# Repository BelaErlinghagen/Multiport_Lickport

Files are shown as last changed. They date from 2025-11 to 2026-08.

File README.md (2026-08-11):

# The Multiport Setup

**A behavioral setup for mice with 16 reward ports, multiple light/sound cues and real time pose estimation.**

<p align="center">
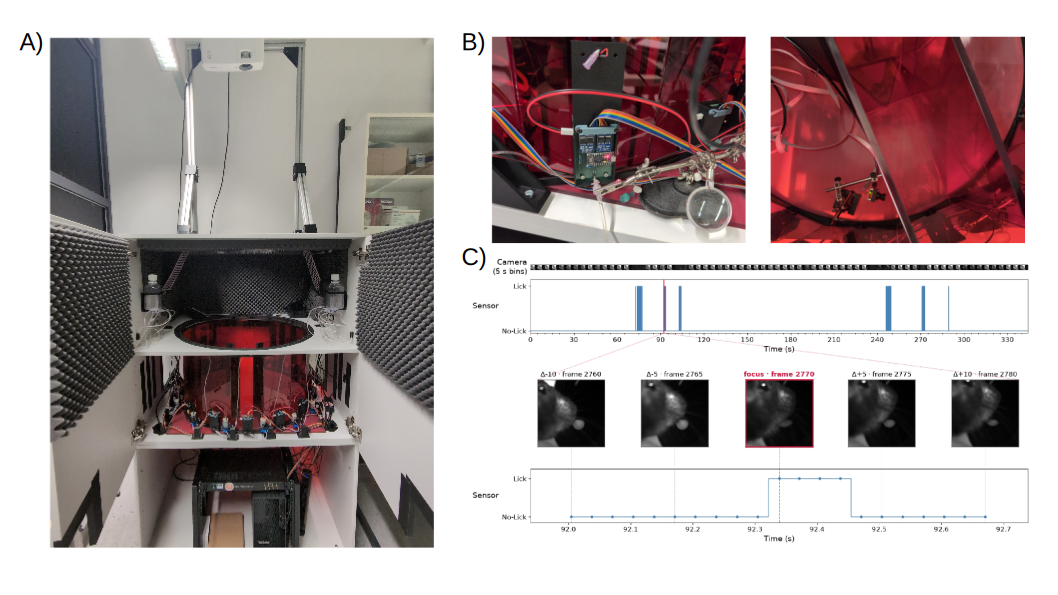
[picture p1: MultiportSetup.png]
Overview of the Multiport Setup
  
</p>

<p align="center">
  <em>
    <b>Figure 1: The Multiport Setup.</b>
    <b>A)</b> Complete view of the Multiport Setup.
    <b>B)</b> Testing adjustments to the setup to show that the capacitive sensor of the Lick-O-Tron detects mouse licks.
    A Basler daA1440 was used to record the lickport. The mouse was given condensed milk (white droplet in C) manually through the shown tube.
    <b>C)</b> <i>Top:</i> Timeline over the entire session, with sensor activations marked as blue bars.
    <i>Bottom:</i> Zoom into one lick detection.
  </em>
</p>

---

## Table of Contents

- [Components of the Multiport Setup](#components-of-the-multiport-setup)
  - [Arena](#arena)
  - [Lick-O-Tron and PORTMASTER](#lick-o-tron-and-portmaster)
  - [Computer](#computer)
  - [Projector](#projector)
  - [Camera](#camera)
  - [Screens](#screens)
- [The Lick-O-Tron Lickport](#the-lick-o-tron-lickport)
  - [Design](#design)
  - [Assembly](#assembly)
    - [Parts](#parts)
    - [Step 1: Soldering](#step-1-soldering)
    - [Step 2: Uploading the code and testing the sensor](#step-2-uploading-the-code-and-testing-the-sensor)
    - [Step 3: Preparing the cannula](#step-3-preparing-the-cannula)
    - [Step 4: Assembly](#step-4-assembly)
    - [Step 5: Add the pump](#step-5-add-the-pump)
  - [Usage](#usage)
- [The PORTMASTER](#the-portmaster)
  - [Design](#design-1)
  - [Assembly](#assembly-1)
    - [Parts](#parts-1)
    - [Step 1: Solder pins and connector pieces to the PCB](#step-1-solder-pins-and-connector-pieces-to-the-pcb)
    - [Step 2: Wiring](#step-2-wiring)
  - [Usage](#usage-1)
- [Credit](#credit)

---

## Components of the Multiport Setup

### Arena

The arena is built from 16 [red acrylic wall panels](ArenaFiles/ArenaWall.stp), held together by 16 [connector pieces](ArenaFiles/AnglePiece.stp). This circular assembly stands on a sheet of acrylic that has been roughened on one side, which makes it more comfortable for the mice to walk on and prevents light projected onto the arena floor from being reflected.

In addition to the circular Multiport arena, two inlets were created to form a Y-Maze.

### Lick-O-Tron and PORTMASTER

The **Lick-O-Tron** is a self-built lickport module consisting of a capacitive sensor, an LED and a MOSFET relay to trigger a pump or valve.

The **PORTMASTER** is a hub that connects all Lick-O-Trons to the master Arduinos and delivers power to the pumps.

Both components are documented in detail below: see [The Lick-O-Tron Lickport](#the-lick-o-tron-lickport) and [The PORTMASTER](#the-portmaster).

### Computer

The computer used in this build was a Lenovo Thinkstation with the following specifications:

| Component | Specification |
| :--- | :--- |
| CPU | Intel(R) Core(TM) i7-14700K |
| GPU | Nvidia GeForce RTX 4060 |
| OS  | Ubuntu 24.04 |

To run live inference with DeepLabCut, CUDA was installed alongside the necessary Nvidia GPU drivers. Pixi was used to manage the Python environment of the software; the `.lock` and `.toml` files can be found in this repository.

### Projector

A BenQ Cinema Master Projector was mounted approximately 200 cm above the arena floor.

### Camera

A Basler daA3840-45uc camera with an Evetar lens (E3417A F2.4 f2.5mm 1/1.8") was mounted 40 cm below the arena floor.

### Screens

In the Y-Maze configuration, two Adafruit screens (5" 800x480 HDMI Backpack) were used to display patterns for the mice. The screens were mounted on [custom holders](ArenaFiles/YMaze_ScreenHolder.stp) that fit the Y-Maze configuration, and were connected directly to the computer via HDMI.

---

# Documentation for the Lick-O-Tron and the PORTMASTER

The Lick-O-Tron lickport and the PORTMASTER connectivity board are the two major components that act together in the automated Multiport system. Their design, assembly and usage are explained in detail below. The files needed to recreate the two modules can be found in their respective folders.

## The Lick-O-Tron Lickport

The idea behind the Lick-O-Tron was to create a lickport for behavioral mouse experiments that can:

1. Register lick events via a capacitive sensor.
2. Connect to up to two peristaltic pumps, which can independently eject precise volumes of liquid.
3. Allow flexible control of an LED located next to the needle.

### Design

The Lick-O-Tron contains three submodules: one Arduino proMicro and two MOSFET relay modules. The Arduino proMicro, as well as the power outlets of the MOSFET relay modules, receive power via the main connector (8-pin plug).

The Arduino's job is to register licks via a capacitive sensor — a cannula connected to the single pin at the bottom of the Lick-O-Tron. This is achieved with the code found [here](Lick-O-Tron/LickportArduinoCode.ino). The Arduino then transmits binary data about lick events to the Arduino Megas housed on the PORTMASTER.

The MOSFET modules are activated by the master Arduinos on the PORTMASTER and can trigger peristaltic pumps (or valves, etc.). The idea is that lick information is received by the master Arduinos, which then activate the pumps at set timepoints and with set PWM, depending on the needs of the experimenter. This allows for very flexible control of liquid dispensation. The Lick-O-Tron further connects the master Arduinos to an LED, which can be controlled independently.

<p align="center">
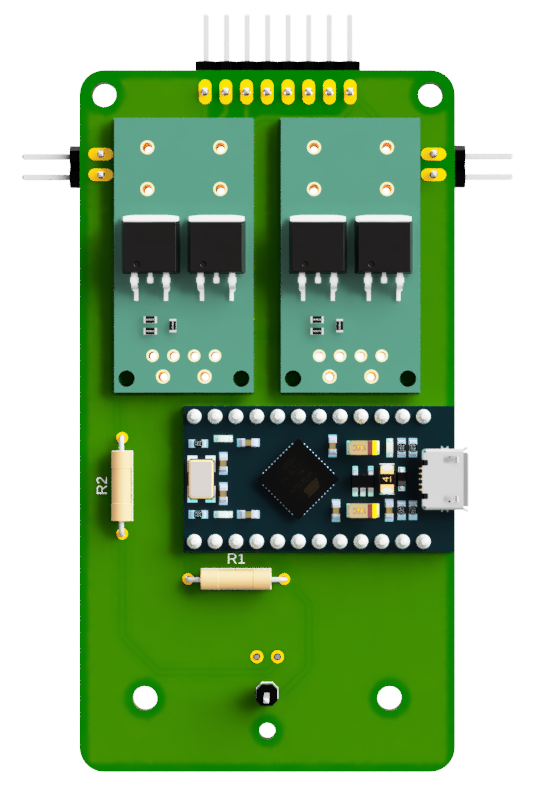
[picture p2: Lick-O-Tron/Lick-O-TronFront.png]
Lick-O-Tron front
  
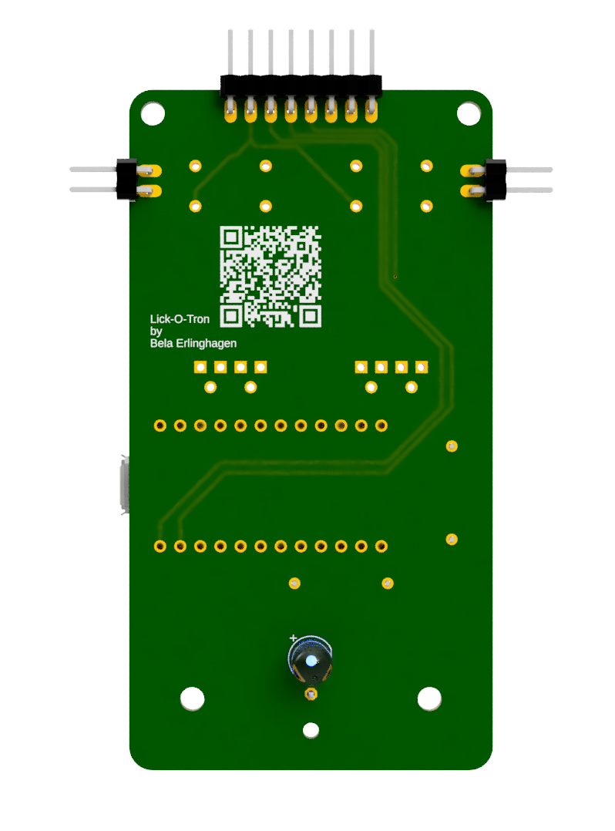
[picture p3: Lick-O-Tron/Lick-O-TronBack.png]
Lick-O-Tron back
  
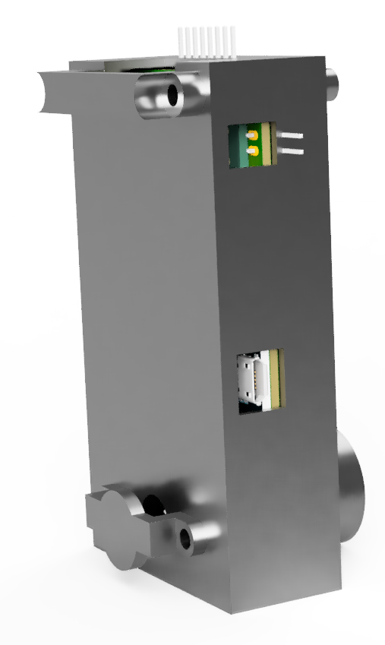
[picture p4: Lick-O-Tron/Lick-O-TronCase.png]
Lick-O-Tron case
  
</p>

<p align="center">
  <em><b>Figure 2:</b> 3D CAD model renderings for the Lick-O-Tron (left: front, middle: back, right: case). Note that the Pin Connectors are not depicted correctly in this Figure: The 8 Pin Header is straight and supposed to be soldered onto the other side of the PCB and the two angular 2 Pin Headers are also depicted on the wrong side of the PCB.</em>
</p>

### Assembly

#### Parts

| Item | Quantity | Manufactured by | EAN |
| :--- | ---: | :--- | ---: |
| Joy It proMicro | 1 | Joy It | 4250236822907 |
| MOSFET Relay Module | 2 | for example GERUI | 0744243396666 |
| Mini Peristaltic Pump | 1 (up to 2) | Whadda | 5410329730017 |
| Lick-O-Tron PCB | 1 | Eurocircuits | None: see folder in repo |
| Lick-O-Tron Case Parts | 1 each | 3D printed | None: see folder in repo |
| LED (white) | 1 | TRU Components | 2050004902785 |
| 10 MOhm Resistor (R1) | 1 | TRU Components | 2050004926057 |
| 470 Ohm Resistor (R2) | 1 | TRU Components | 4016139313023 |
| M3 Screws | 4 | Toolcraft | 4064161107578 |
| M3 Nuts | 4 | SWG Hox | 4053056028951 |
| Sterican Cannula | 2 | Roth | - |

#### Step 1: Soldering

With the PCB, the proMicro, the LED, the resistors, some pins and the relay modules at hand, the first step is to solder all of these components onto the PCB. By the end, the PCB should look similar to what is shown in Figure 2.

#### Step 2: Uploading the code and testing the sensor

Upload the Lick-O-Tron [code](Lick-O-Tron/LickportArduinoCode.ino) from this repository to the Joy It proMicro using the Arduino IDE. Then use the serial monitor to test whether touching the sensor pin registers something.

#### Step 3: Preparing the cannula

<p align="center">
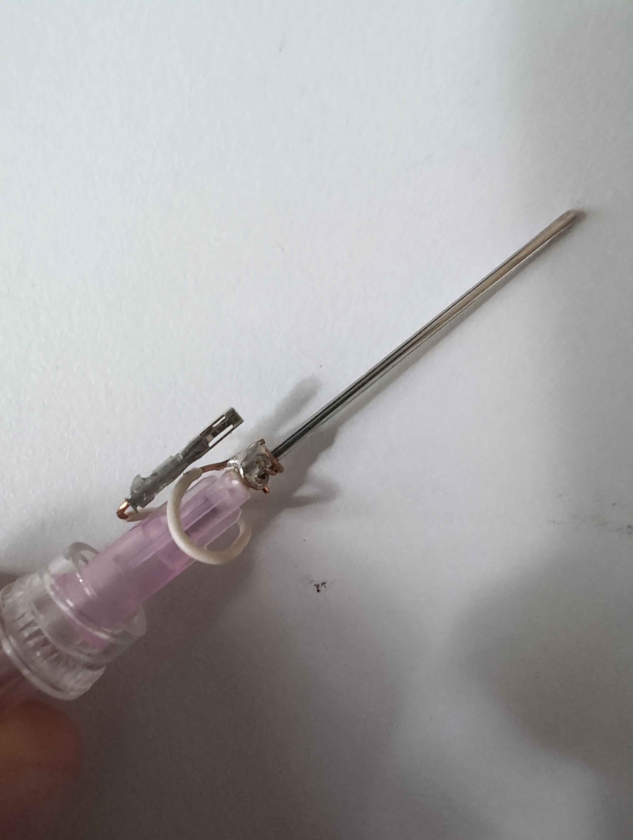
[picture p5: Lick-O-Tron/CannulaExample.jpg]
Example cannula assembly
  
</p>

<p align="center">
  <em><b>Figure 3:</b> Example cannula assembly.</em>
</p>

To electrically connect the cannula to the sensor pin, a wire was wrapped around the cannula and clamped to it, and a second wire was then soldered onto the first one. This second wire was soldered to a pin connector piece, which connects to the sensor pin.

#### Step 4: Assembly

Once all these pieces are ready, the Lick-O-Tron can be assembled. In the Multiport build previewed here, the PCB was simply placed into the 3D-printed chamber and everything was screwed together directly onto the arena, where the spout frame had already been fixed into the acrylic sheets.

#### Step 5: Add the pump

To add the pump, solder two wires to the solder flags and their other ends to a pin connector. To rebuild the setup shown here exactly, 3D print the pump holder pieces and attach the pump as shown in Figure 4.

### Usage

<p align="center">
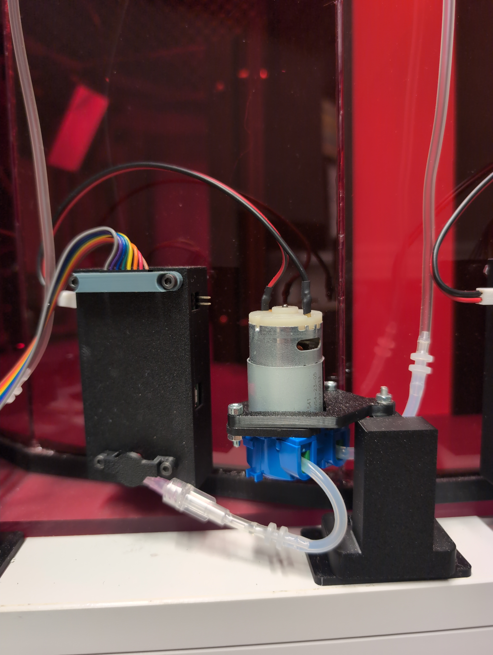
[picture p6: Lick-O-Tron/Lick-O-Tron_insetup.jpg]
Assembled Lick-O-Tron in the setup
  
</p>

<p align="center">
  <em><b>Figure 4:</b> All pieces together.</em>
</p>

The Lick-O-Tron is connected to the PORTMASTER via an 8-band ribbon cable. One PORTMASTER can control up to 16 Lick-O-Trons.

---

## The PORTMASTER

<p align="center">
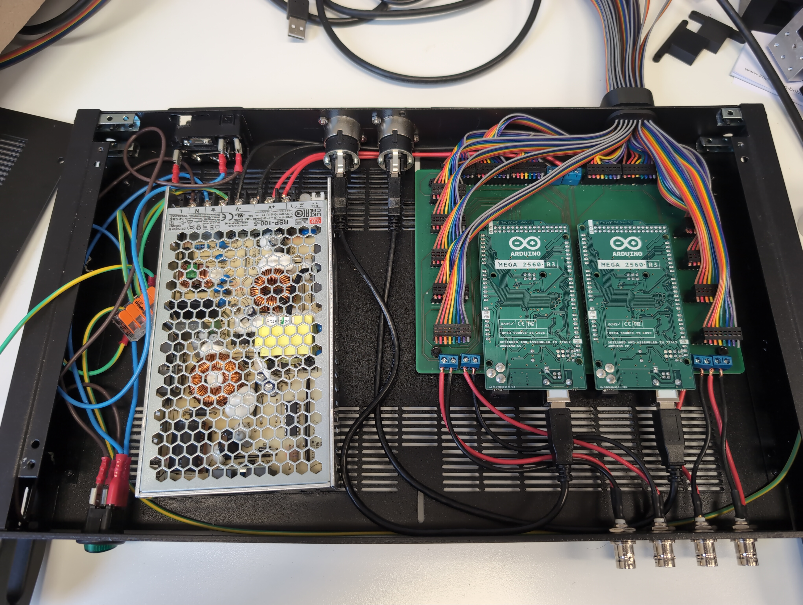
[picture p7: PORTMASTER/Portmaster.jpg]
The PORTMASTER rack with the lid opened
  
</p>

<p align="center">
  <em><b>Figure 5:</b> The PORTMASTER rack, lid opened.</em>
</p>

### Design

The PORTMASTER is designed to:

- power up to five 6 V pumps comfortably (more are possible);
- provide an easily accessible interface between the Arduinos and the computer, BNCs and power supply.

### Assembly

#### Parts

| Item | Quantity | Manufactured by | EAN |
| :--- | ---: | :--- | ---: |
| Arduino Mega 2560 Rev3 | 2 | Arduino | 7630049200067 |
| 8-band ribbon cable | - | - | - |
| 8-Way IDC Connector Female for Cable, 1 Row | 32 | Wurth Elektronik | 661008151923 (Mf. part #) |
| PORTMASTER PCB | 1 | Eurocircuits | None: see folder in repo |
| RSP-100-5 SMPSU 5V DC 20A 100W | 1 | MEAN WELL | 4711287435657 |

> **Note:** The remaining parts visible in Figure 5 have been left out on purpose, as they are specific to the space in which the Multiport Setup — and especially the PORTMASTER — was housed.

#### Step 1: Solder pins and connector pieces to the PCB

To connect the two Arduino Megas to the PCB, first solder the pins and the connector pieces for the power supply and the BNCs onto the PCB.

#### Step 2: Wiring

Once the Arduinos are in place, all that is left to do is the wiring. The 16 Lick-O-Trons are connected using an 8-band ribbon cable together with two 8-way IDC connectors, one going on the Lick-O-Tron and one on the PORTMASTER. Then the power supply needs to be connected to mains power and to the PCB. In the build showcased here, male BNC plugs were also connected to the PCB.

> **Safety:** Make sure to properly ground the casing of the PORTMASTER.

### Usage

The PORTMASTER can be connected to a computer via two USB-B to USB-A cables. It can then be used with the [custom software](Multiport_Code) in this repository.

---

## Credit

The Lick-O-Tron and the PORTMASTER were conceptualized and designed by Bela Erlinghagen, with extensive support from [Trace Robbins](https://github.com/R-Trace) and [Ben Escribano](https://github.com/BenjaminEscribano) of the iBehave CADRE ([website](https://ibehave.nrw/ibots-platform/cadre/), [GitHub](https://github.com/iBehave-CADRE)).

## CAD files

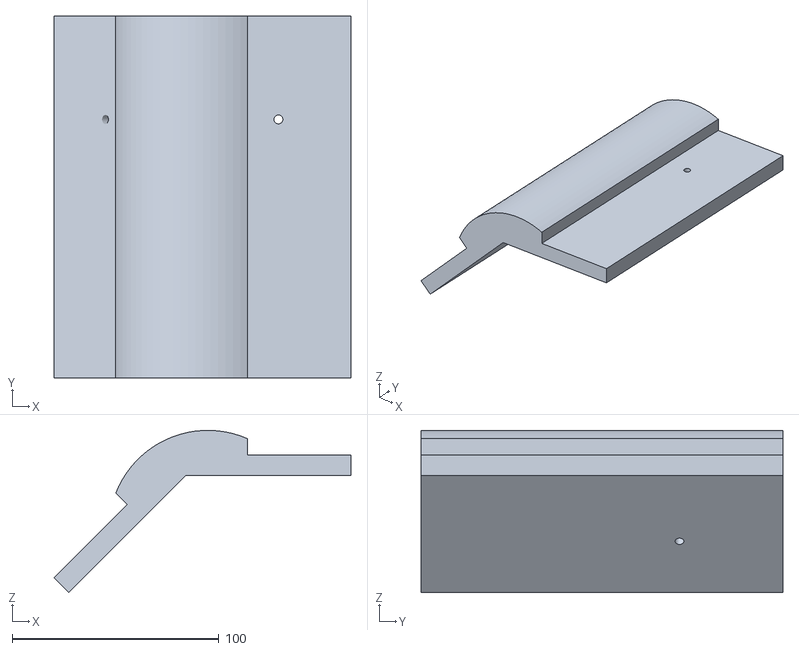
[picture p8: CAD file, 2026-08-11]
ArenaFiles/Y_MazeSidepieceTop.stl
143.6 x 175.0 x 78.4

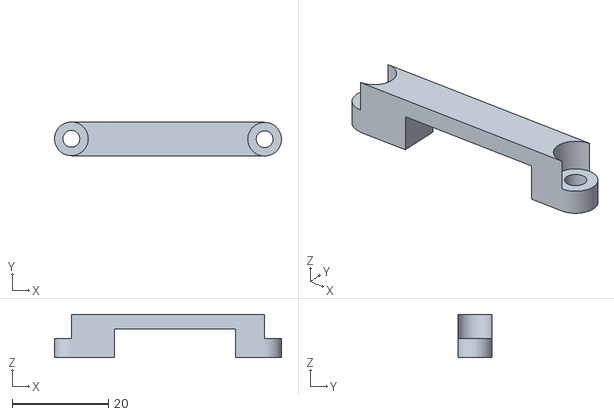
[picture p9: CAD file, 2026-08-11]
Lick-O-Tron/LickOTron_RibbonCableHolder.stl
47.1 x 7.08 x 9.00

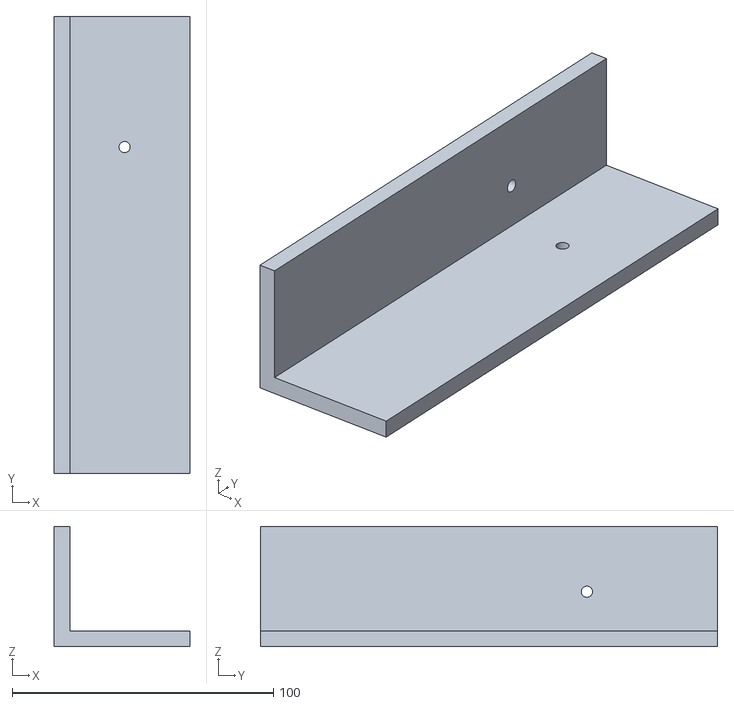
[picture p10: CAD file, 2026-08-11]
ArenaFiles/Y_MazeBackPieceTopLeft.stl
52.0 x 175.0 x 46.0

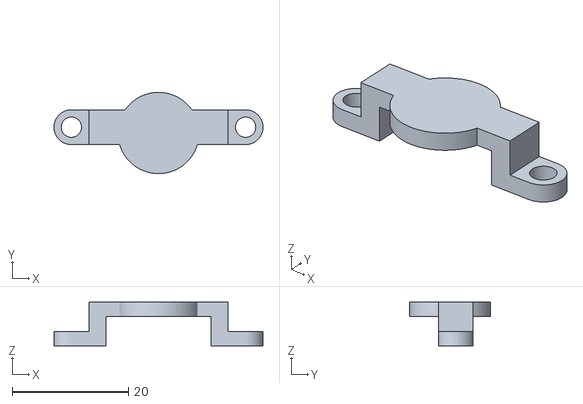
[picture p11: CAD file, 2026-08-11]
Lick-O-Tron/LickOTron_CannulaClamp.stl
36.0 x 14.0 x 7.50

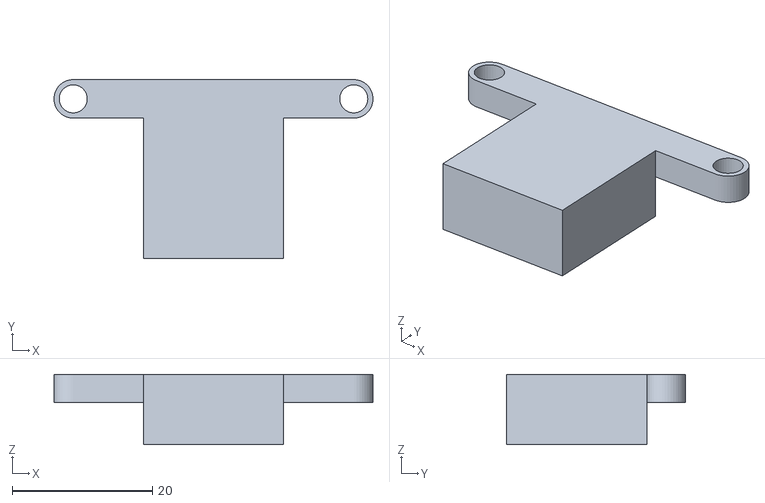
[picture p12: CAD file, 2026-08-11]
Lick-O-Tron/LickOTron_ArenaDistancePiece.stl
45.5 x 25.5 x 10.0

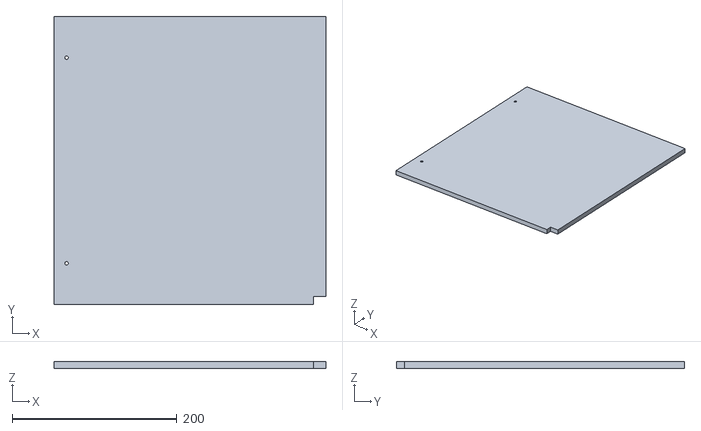
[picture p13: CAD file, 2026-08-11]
ArenaFiles/YMazeWall.stl
330.0 x 350.0 x 8.00

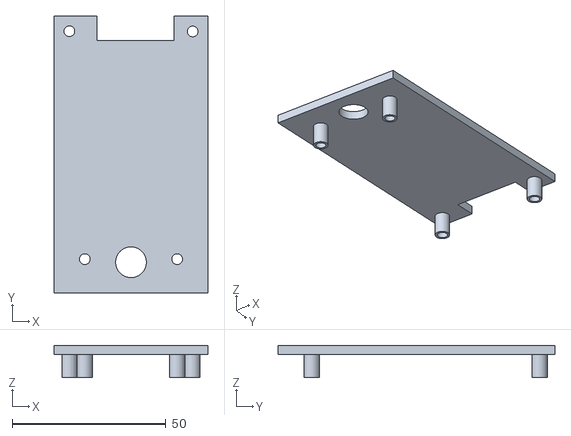
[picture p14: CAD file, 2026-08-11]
Lick-O-Tron/LickOTronCaseTop.stl
50.0 x 90.0 x 10.4

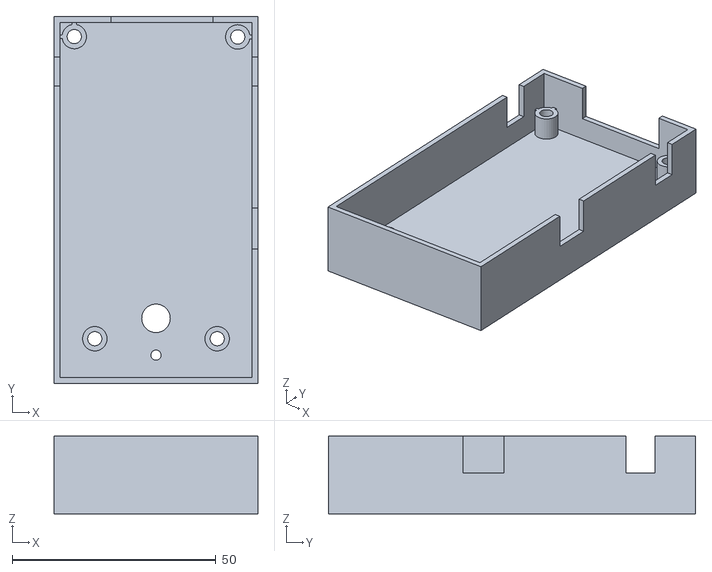
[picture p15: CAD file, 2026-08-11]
Lick-O-Tron/LickOTronCaseBody.stl
50.0 x 90.0 x 19.0

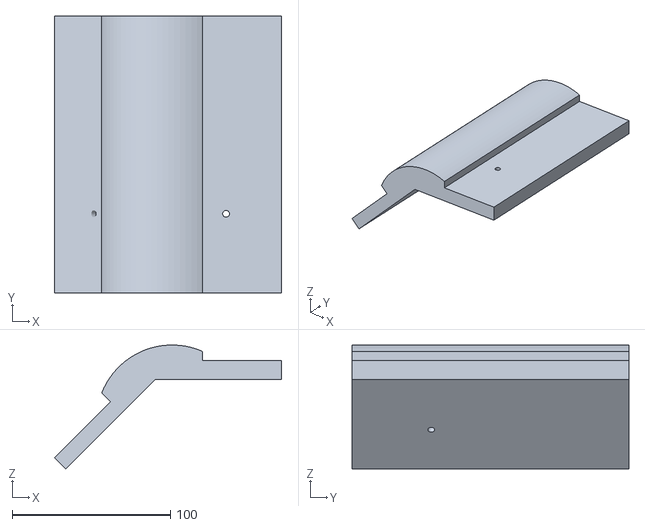
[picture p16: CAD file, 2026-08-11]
ArenaFiles/Y_MazeSidepieceBottom.stl
143.6 x 175.0 x 78.4

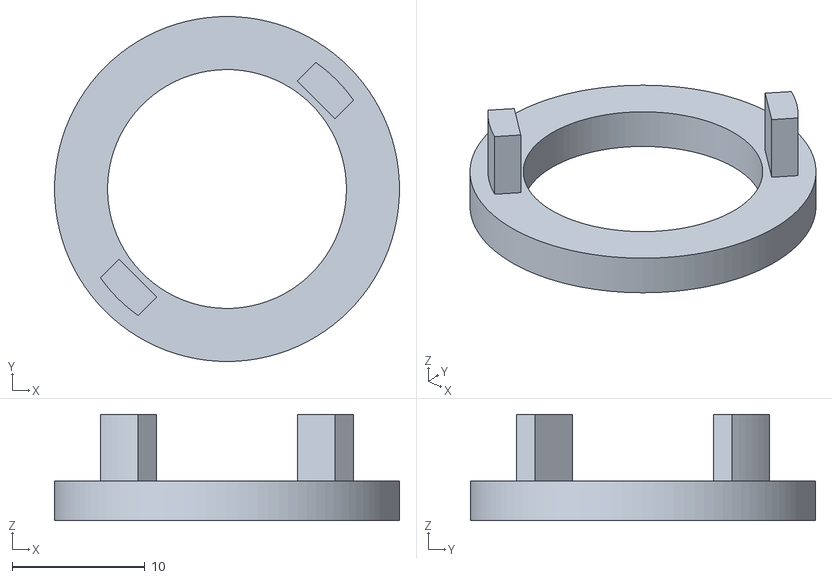
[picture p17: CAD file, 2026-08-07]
Lick-O-Tron/LickspoutWithinArenaPiece.stl
26.0 x 26.0 x 8.00

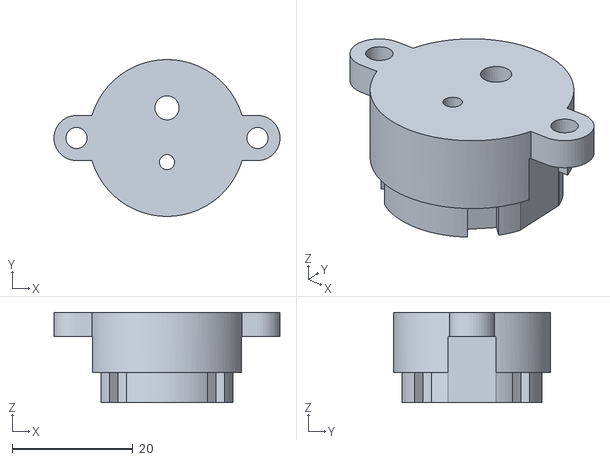
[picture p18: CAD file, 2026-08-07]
Lick-O-Tron/LickspoutOuterPiece.stl
37.5 x 26.0 x 15.0

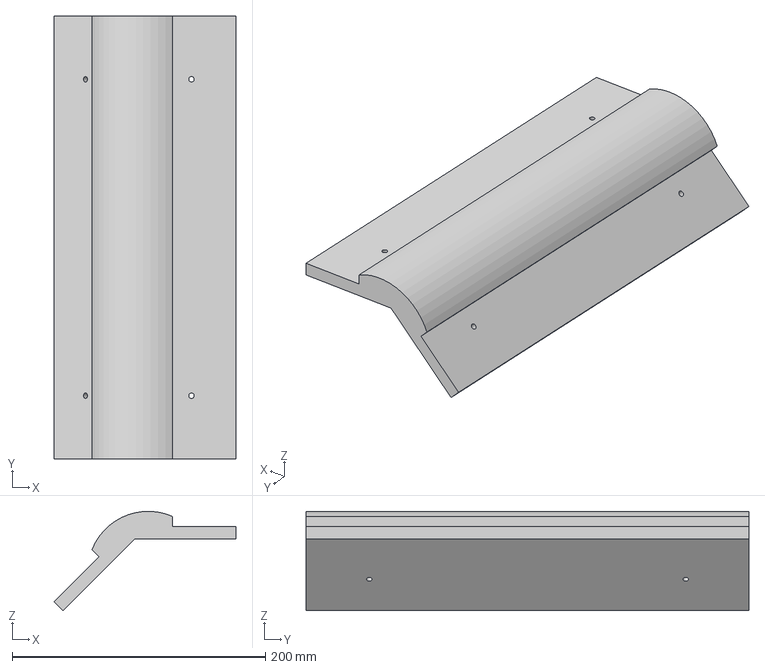
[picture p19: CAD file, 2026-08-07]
ArenaFiles/YMaze_MiddlePiece.stp
143.6 x 350.0 x 78.4 mm

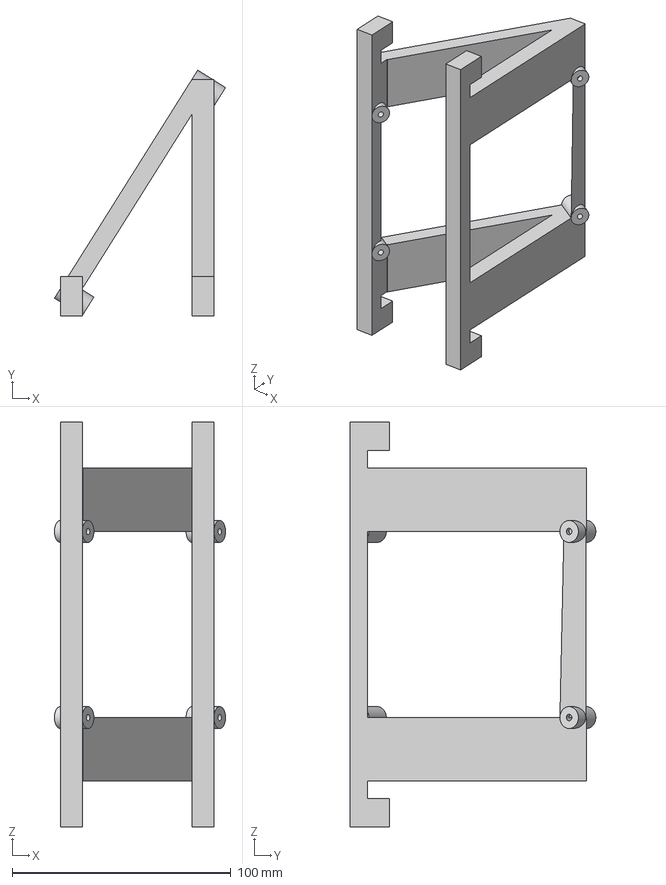
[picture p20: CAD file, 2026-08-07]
ArenaFiles/YMaze_ScreenHolder.stp
78.1 x 112.2 x 185.0 mm

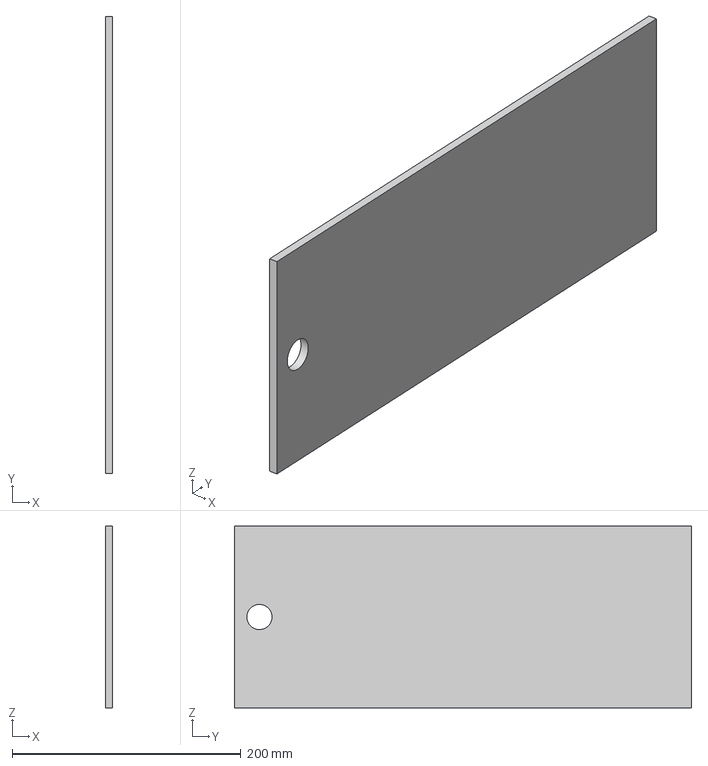
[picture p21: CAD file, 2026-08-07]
ArenaFiles/ArenaWall.stp
6.00 x 400.0 x 159.1 mm

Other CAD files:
ArenaFiles/Y_MazeBackPieceTopRight.stl
ArenaFiles/Y_MazeBackpieceBottomLeft.stl
ArenaFiles/Y_MazeBackPieceBottomRight.stl
ArenaFiles/AnglePiece.stp

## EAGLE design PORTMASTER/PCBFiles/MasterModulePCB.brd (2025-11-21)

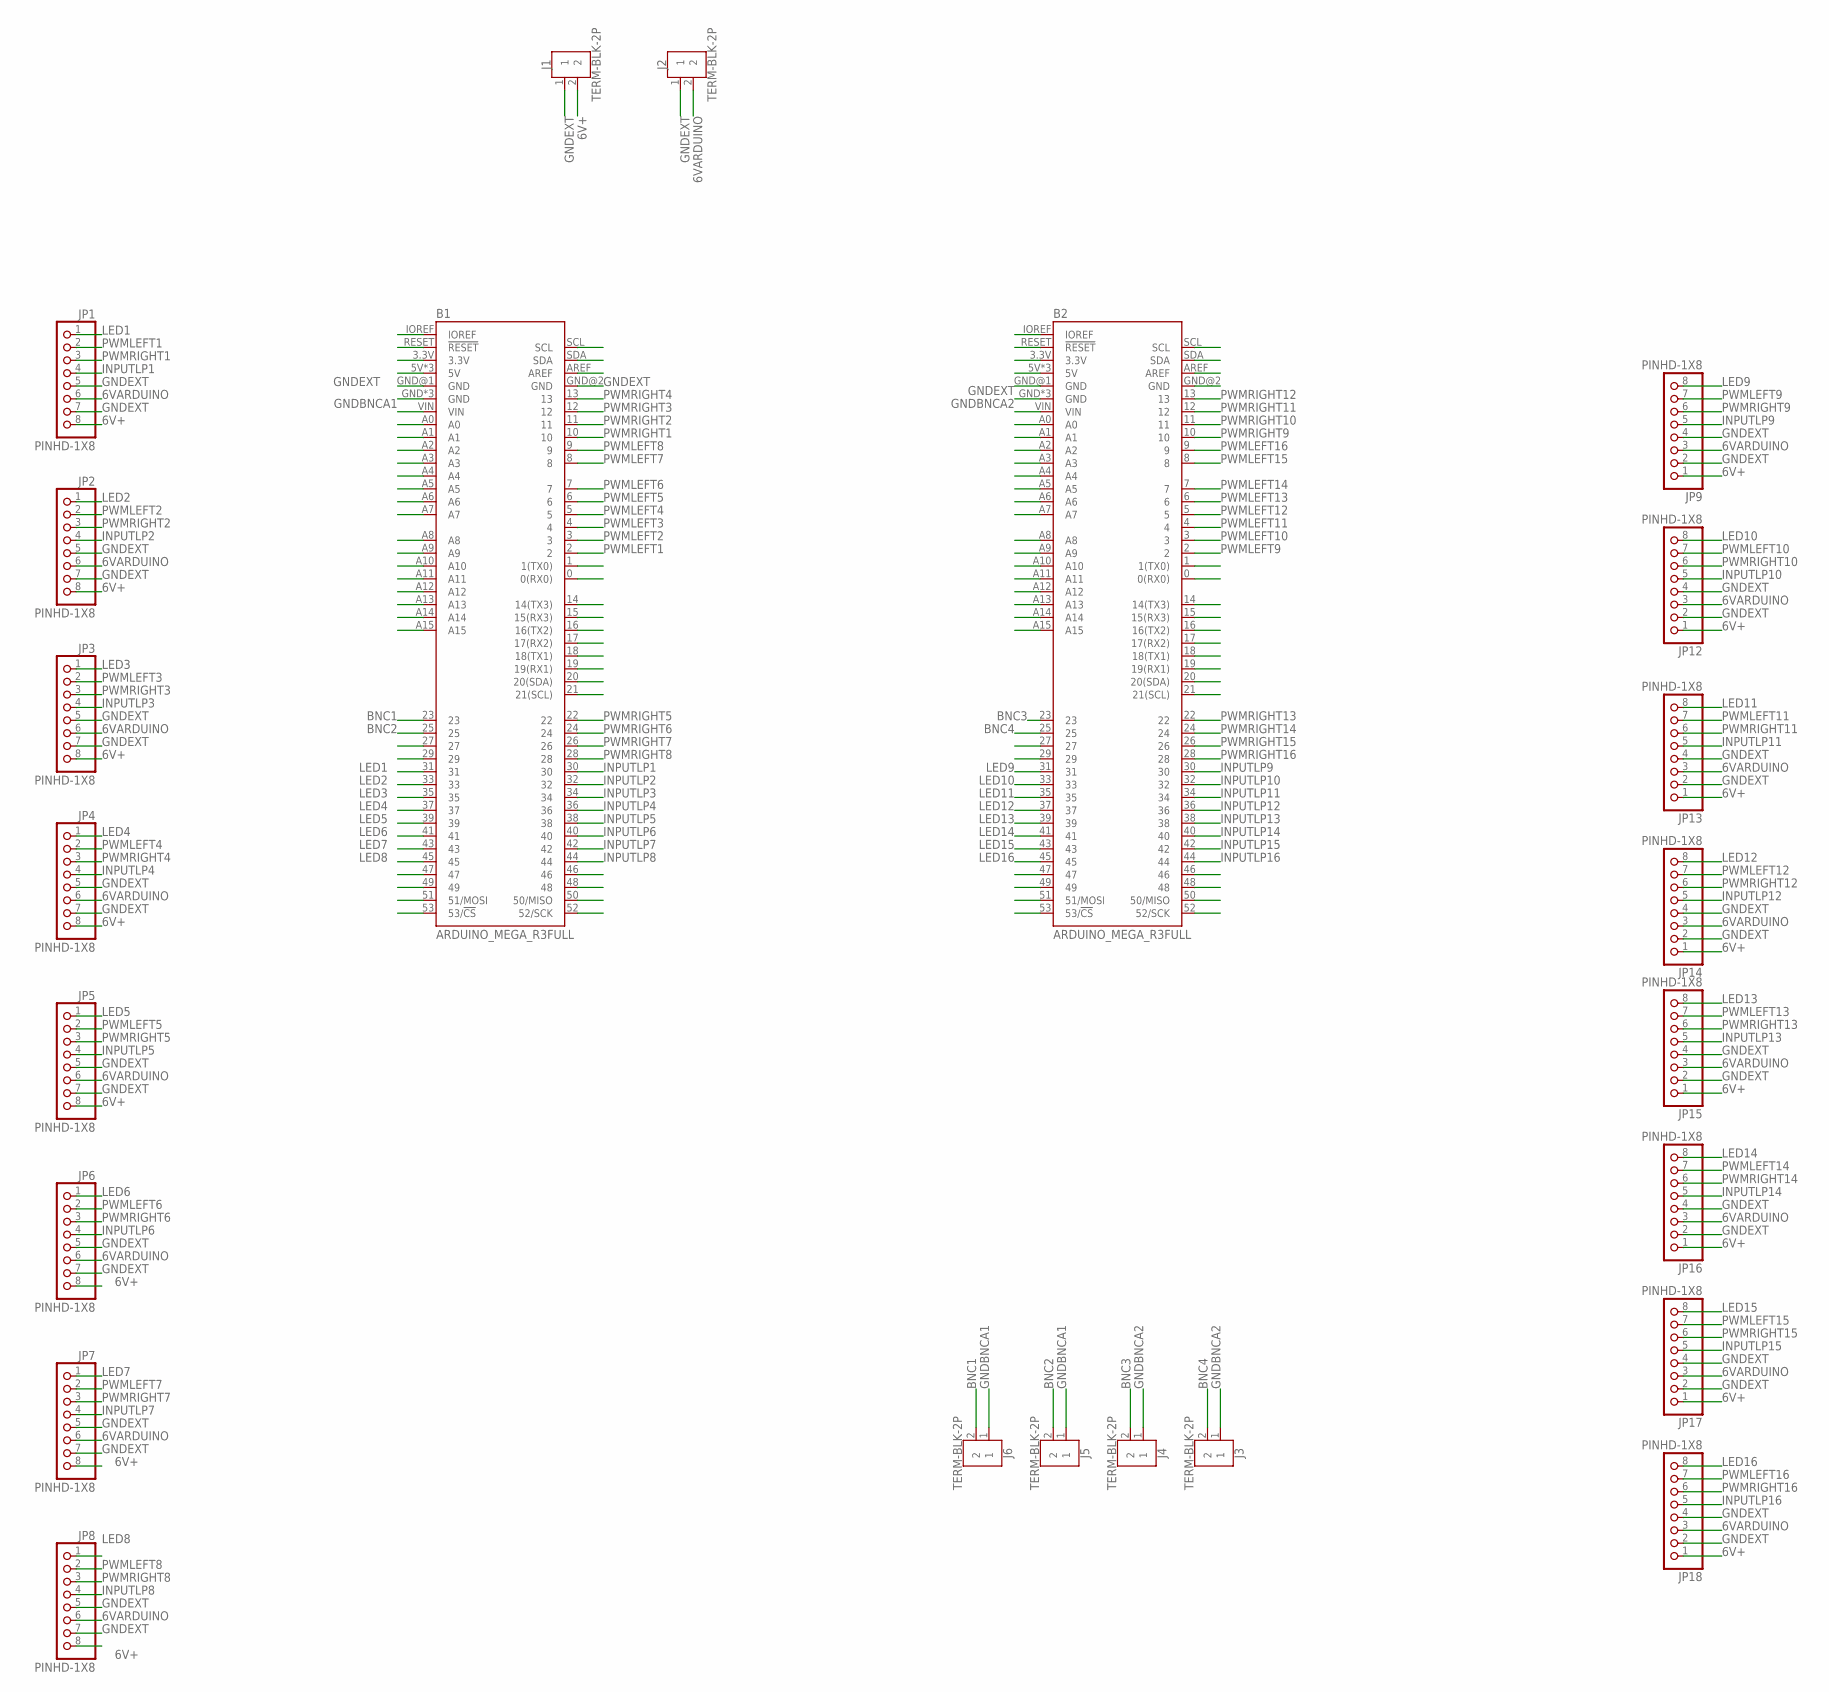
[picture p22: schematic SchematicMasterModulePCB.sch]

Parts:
B1, B2: ARDUINO_MEGA_R3FULL; ARDUINO_MEGA_NO_SILK
J1, J2, J3, J4, J5, J6: TERM-BLK-2P; TERMBLK_508-2N
JP1, JP2, JP3, JP4, JP5, JP6, JP7, JP8, JP9, JP12, JP13, JP14, JP15, JP16, JP17, JP18: PINHD-1X8; 1X08

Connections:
6V+: J1.2, JP1.8, JP2.8, JP3.8, JP4.8, JP5.8, JP6.8, JP7.8, JP8.8, JP9.1, JP12.1, JP13.1, JP14.1, JP15.1, JP16.1, JP17.1, JP18.1
6VARDUINO: J2.2, JP1.6, JP2.6, JP3.6, JP4.6, JP5.6, JP6.6, JP7.6, JP8.6, JP9.3, JP12.3, JP13.3, JP14.3, JP15.3, JP16.3, JP17.3, JP18.3
BNC1: B1.23, J6.2
BNC2: B1.25, J5.2
BNC3: B2.23, J4.2
BNC4: B2.25, J3.2
GNDBNCA1: B1.GND, B1.GND@3 (GND), B1.GND@4 (GND), J5.1, J6.1
GNDBNCA2: B2.GND, B2.GND@3 (GND), B2.GND@4 (GND), J3.1, J4.1
GNDEXT: B1.GND@1 (GND), B1.GND@2 (GND), B2.GND@1 (GND), J1.1, J2.1, JP1.5, JP1.7, JP2.5, JP2.7, JP3.5, JP3.7, JP4.5, JP4.7, JP5.5, JP5.7, JP6.5, JP6.7, JP7.5, JP7.7, JP8.5, JP8.7, JP9.2, JP9.4, JP12.2, JP12.4, JP13.2, JP13.4, JP14.2, JP14.4, JP15.2, JP15.4, JP16.2, JP16.4, JP17.2, JP17.4, JP18.2, JP18.4
INPUTLP1: B1.30, JP1.4
INPUTLP2: B1.32, JP2.4
INPUTLP3: B1.34, JP3.4
INPUTLP4: B1.36, JP4.4
INPUTLP5: B1.38, JP5.4
INPUTLP6: B1.40, JP6.4
INPUTLP7: B1.42, JP7.4
INPUTLP8: B1.44, JP8.4
INPUTLP9: B2.30, JP9.5
INPUTLP10: B2.32, JP12.5
INPUTLP11: B2.34, JP13.5
INPUTLP12: B2.36, JP14.5
INPUTLP13: B2.38, JP15.5
INPUTLP14: B2.40, JP16.5
INPUTLP15: B2.42, JP17.5
INPUTLP16: B2.44, JP18.5
LED1: B1.31, JP1.1
LED2: B1.33, JP2.1
LED3: B1.35, JP3.1
LED4: B1.37, JP4.1
LED5: B1.39, JP5.1
LED6: B1.41, JP6.1
LED7: B1.43, JP7.1
LED8: B1.45, JP8.1
LED9: B2.31, JP9.8
LED10: B2.33, JP12.8
LED11: B2.35, JP13.8
LED12: B2.37, JP14.8
LED13: B2.39, JP15.8
LED14: B2.41, JP16.8
LED15: B2.43, JP17.8
LED16: B2.45, JP18.8
unnamed: B2.5V, B2.5V@1 (5V), B2.5V@2 (5V)
unnamed: B1.5V, B1.5V@1 (5V), B1.5V@2 (5V)
PWMLEFT1: B1.2, JP1.2
PWMLEFT2: B1.3, JP2.2
PWMLEFT3: B1.4, JP3.2
PWMLEFT4: B1.5, JP4.2
PWMLEFT5: B1.6, JP5.2
PWMLEFT6: B1.7, JP6.2
PWMLEFT7: B1.8, JP7.2
PWMLEFT8: B1.9, JP8.2
PWMLEFT9: B2.2, JP9.7
PWMLEFT10: B2.3, JP12.7
PWMLEFT11: B2.4, JP13.7
PWMLEFT12: B2.5, JP14.7
PWMLEFT13: B2.6, JP15.7
PWMLEFT14: B2.7, JP16.7
PWMLEFT15: B2.8, JP17.7
PWMLEFT16: B2.9, JP18.7
PWMRIGHT1: B1.10, JP1.3
PWMRIGHT2: B1.11, JP2.3
PWMRIGHT3: B1.12, JP3.3
PWMRIGHT4: B1.13, JP4.3
PWMRIGHT5: B1.22, JP5.3
PWMRIGHT6: B1.24, JP6.3
PWMRIGHT7: B1.26, JP7.3
PWMRIGHT8: B1.28, JP8.3
PWMRIGHT9: B2.10, JP9.6
PWMRIGHT10: B2.11, JP12.6
PWMRIGHT11: B2.12, JP13.6
PWMRIGHT12: B2.13, JP14.6
PWMRIGHT13: B2.22, JP15.6
PWMRIGHT14: B2.24, JP16.6
PWMRIGHT15: B2.26, JP17.6
PWMRIGHT16: B2.28, JP18.6

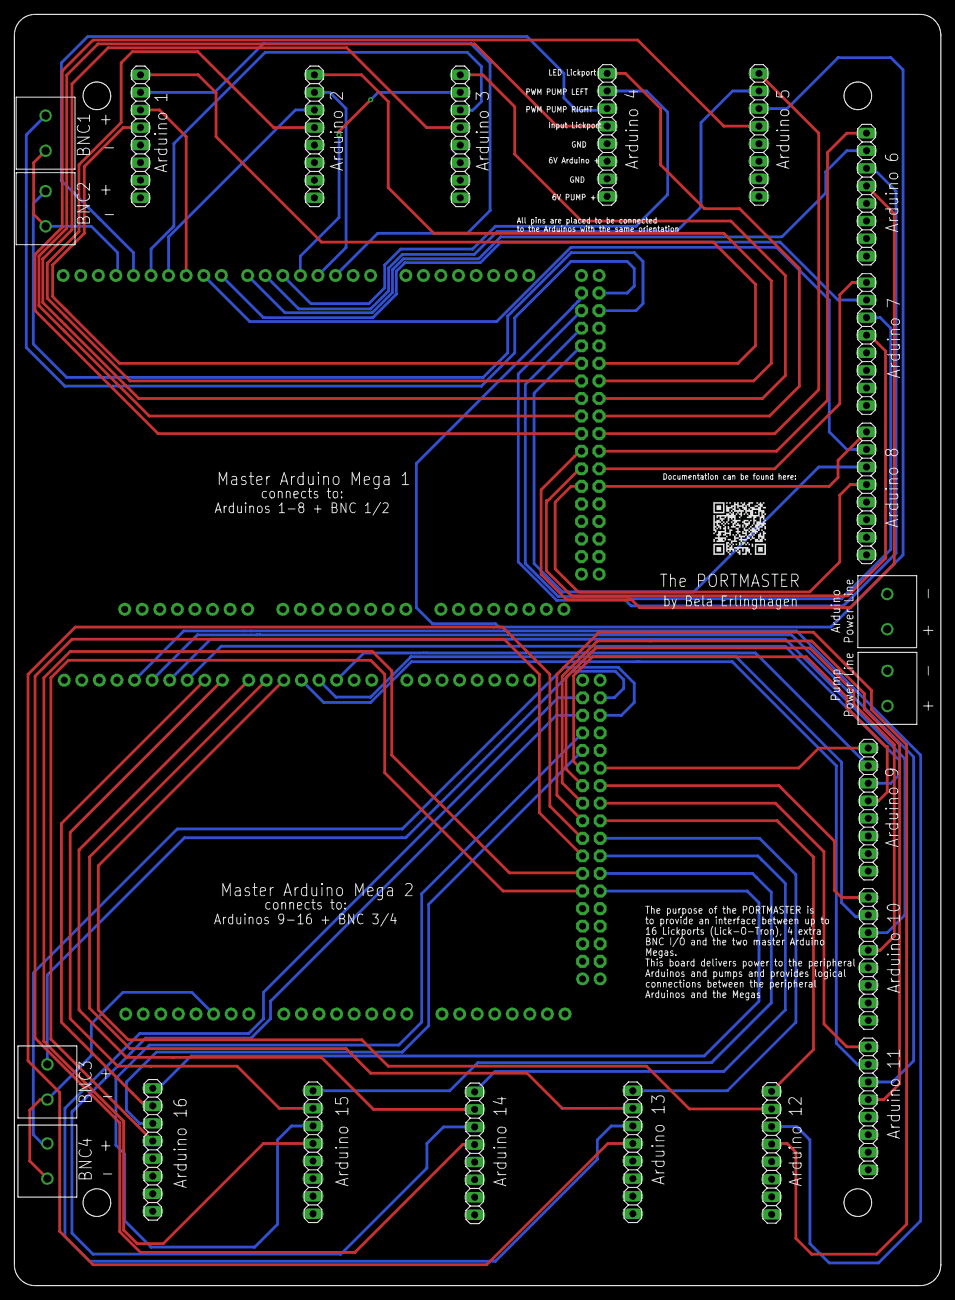
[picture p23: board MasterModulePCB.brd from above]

Board: 4 copper layers, 133.9 x 183.8 mm, 24 parts (0 on the bottom side), 75 nets.

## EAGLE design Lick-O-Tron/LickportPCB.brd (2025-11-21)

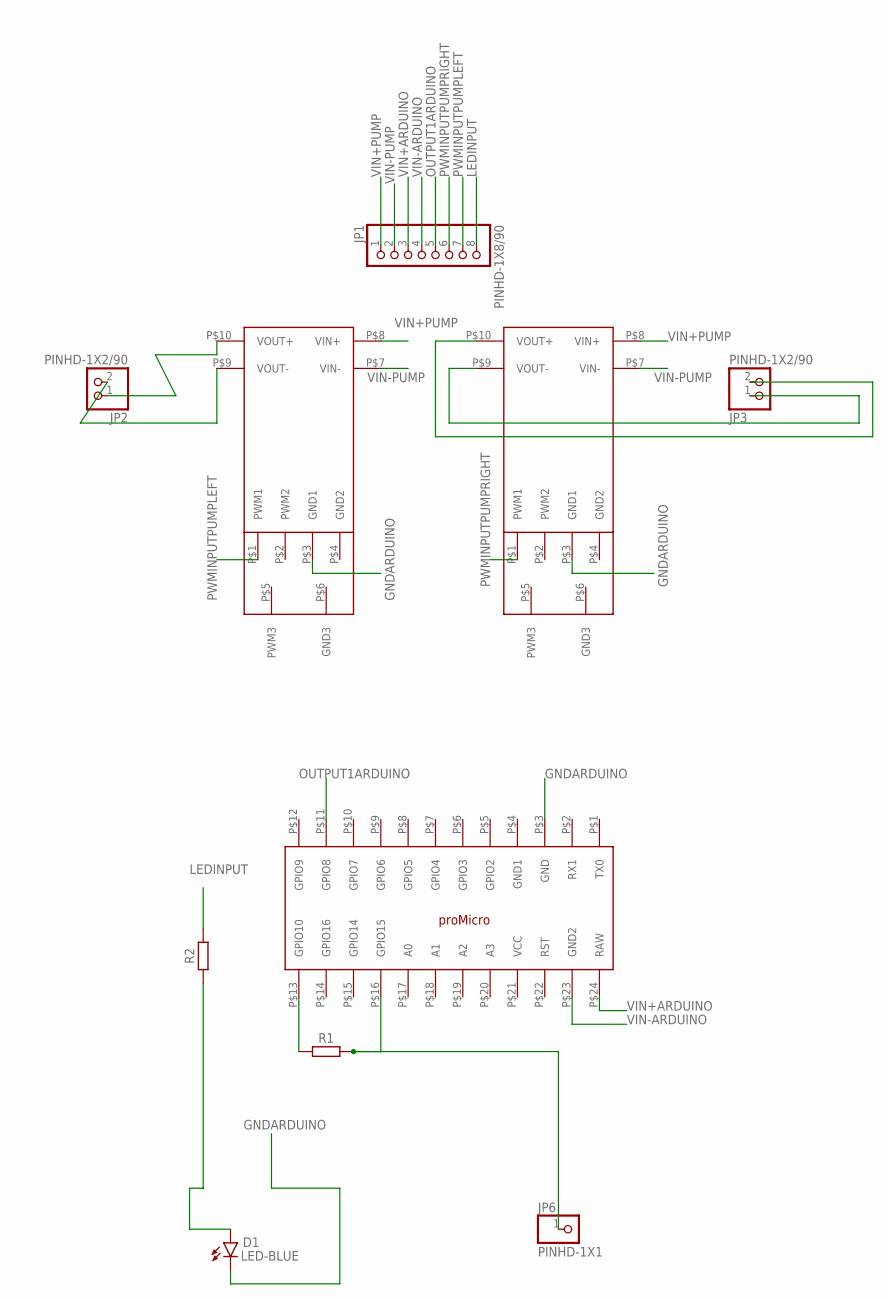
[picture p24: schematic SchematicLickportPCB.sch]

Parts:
D1: LED-BLUE; LEDRD254W60D565H860B_B
JP1: PINHD-1X8/90; 1X08/90
JP2, JP3: PINHD-1X2/90; 1X02/90
JP6: PINHD-1X1; 1X01
R1, R2: RESISTOR_AXIAL-11.7MM-PITCH; RESAD1176W63L850D250B
U$1, U$2: MOSFET_MODULE
U$3: JOY_IT_PRO_MICRO

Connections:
GNDARDUINO: D1.C, U$1.P$3 (GND1), U$2.P$3 (GND1), U$3.P$3 (GND)
LEDINPUT: JP1.8, R2.2
unnamed: JP2.1, U$1.P$10 (VOUT+)
unnamed: JP2.2, U$1.P$9 (VOUT-)
unnamed: JP3.2, U$2.P$10 (VOUT+)
unnamed: JP3.1, U$2.P$9 (VOUT-)
unnamed: D1.A, R2.1
unnamed: R1.1, U$3.P$13 (GPIO10)
unnamed: JP6.1, R1.2, U$3.P$16 (GPIO15)
OUTPUT1ARDUINO: JP1.5, U$3.P$11 (GPIO8)
PWMINPUTPUMPLEFT: JP1.7, U$1.P$1 (PWM1)
PWMINPUTPUMPRIGHT: JP1.6, U$2.P$1 (PWM1)
VIN+ARDUINO: JP1.3, U$3.P$24 (RAW)
VIN+PUMP: JP1.1, U$1.P$8 (VIN+), U$2.P$8 (VIN+)
VIN-ARDUINO: JP1.4, U$3.P$23 (GND2)
VIN-PUMP: JP1.2, U$1.P$7 (VIN-), U$2.P$7 (VIN-)

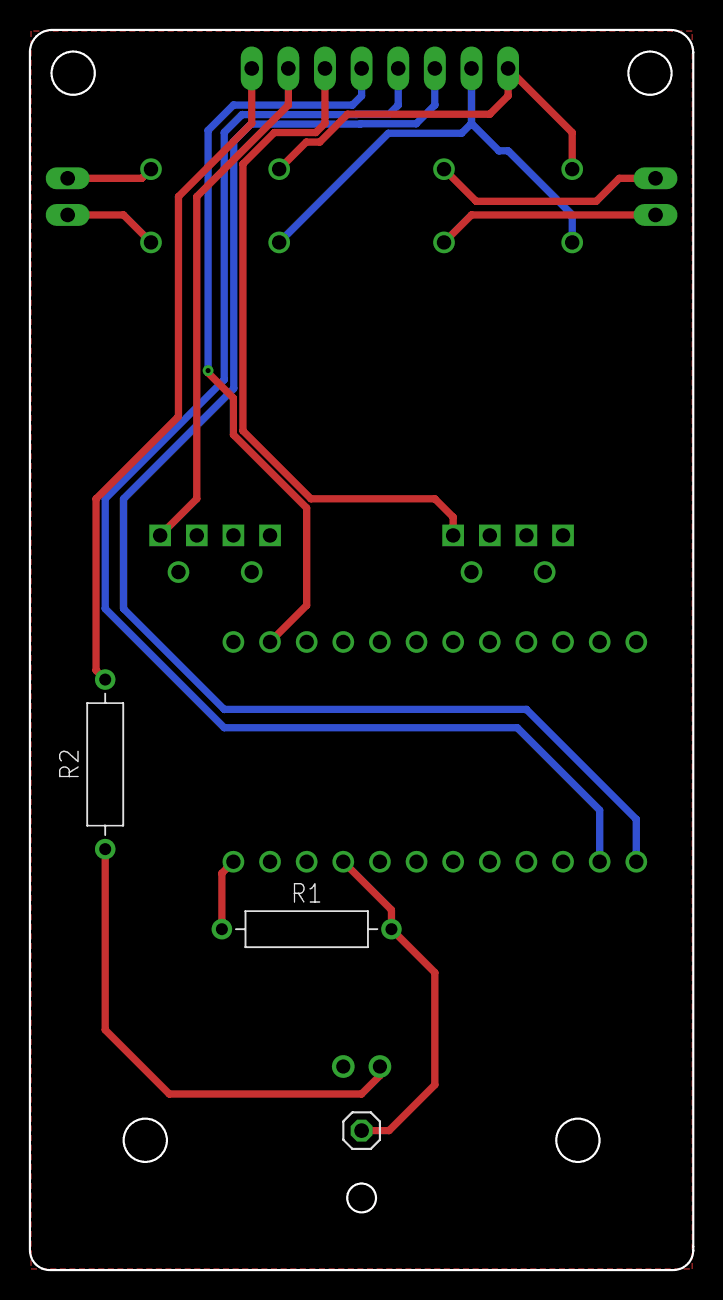
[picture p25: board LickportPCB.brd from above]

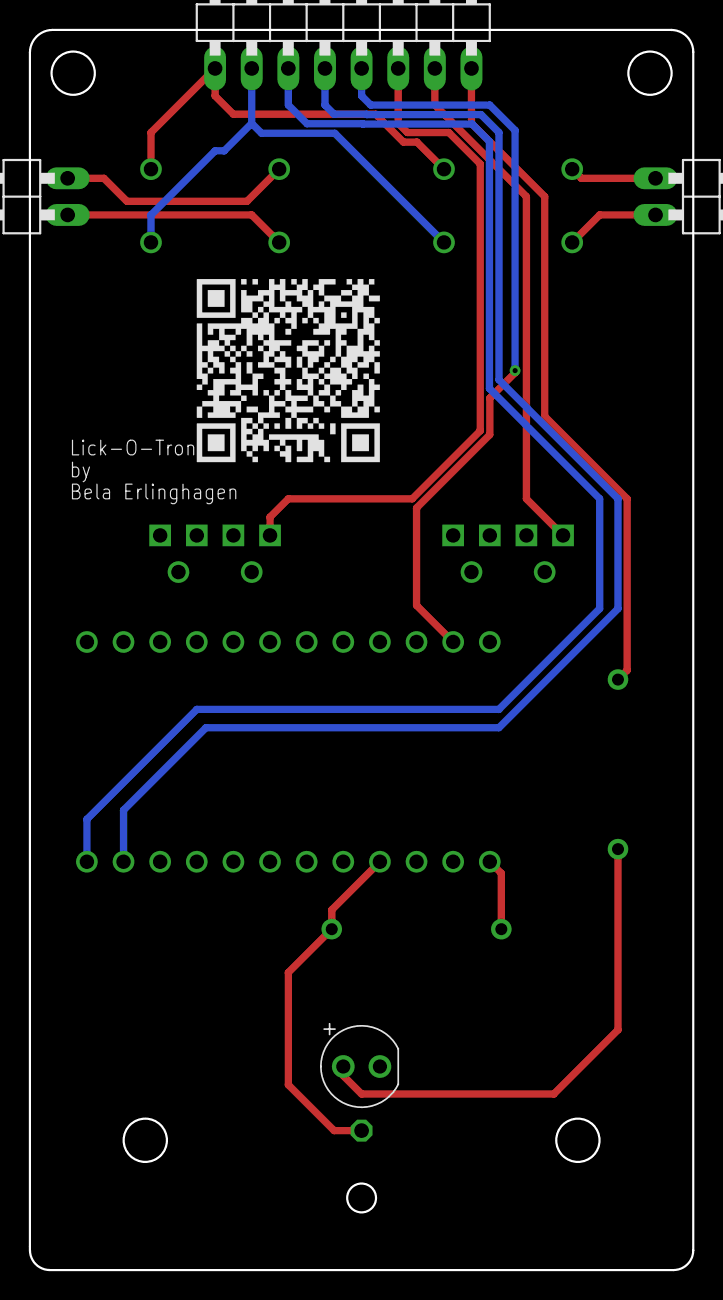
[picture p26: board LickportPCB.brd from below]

Board: 2 copper layers, 46.0 x 86.0 mm, 10 parts (4 on the bottom side), 16 nets.

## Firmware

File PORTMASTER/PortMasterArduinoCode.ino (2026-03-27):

/*
 * 
 * Hardware Configuration:
 * - 8 Inputs (Capacitive Sensors): Pins 30, 32, 34, 36, 38, 40, 42, 44
 * - 8 LEDs: Pins 31, 33, 35, 37, 39, 41, 43, 45
 * - 16 MOSFET Relays: Pins 2, 3, 4, 5, 6, 7, 8, 9, 10, 11, 12, 13, 22, 24, 26, 28
 * - 2 BNC Outputs: Pins 23, 25
 * 
 * Serial Protocol:
 * - Output: STATUS:<timestamp_ms>:<active_pin_numbers>
 *   (e.g., STATUS:1234567890:2 for pin 2 active, or STATUS:1234567890:2,4,7 for multiple)
 * - Input Commands:
 *   LED:<pin_id>:<state>       (state: ON, OFF, or 0-255 for PWM if supported by hardware)
 *   MOS:<pin_id>:<mode>:<duration_ms>
 *      mode: ON, OFF
 *      duration: 0 for continuous, >0 for timed pulse (ms)
 *   BNC:<pin_id>:PULSE:<duration_ms>
 */

// --- Pin Definitions ---
const int INPUT_PINS[] = {30, 32, 34, 36, 38, 40, 42, 44};
const int LED_PINS[]   = {31, 33, 35, 37, 39, 41, 43, 45};
const int MOSFET_PINS[]= {2, 3, 4, 5, 6, 7, 8, 9, 10, 11, 12, 13, 22, 24, 26, 28};
const int BNC_PINS[]   = {23, 25};

// --- Constants ---
const int NUM_INPUTS = 8;
const int NUM_LEDS = 8;
const int NUM_MOSFETS = 16;
const int NUM_BNC = 2;
const unsigned long STATUS_INTERVAL = 100; // Send status every 100ms

// --- State Variables ---
unsigned long lastStatusTime = 0;
bool mosfetActive[NUM_MOSFETS] = {false};
unsigned long mosfetEndTime[NUM_MOSFETS] = {0};

// BNC Timer Variables (moved to global scope for persistence)
bool bncActive[NUM_BNC] = {false};
unsigned long bncEndTime[NUM_BNC] = {0};

void setup() {
  Serial.begin(115200);
  
  // Initialize Inputs
  for (int i = 0; i < NUM_INPUTS; i++) {
    pinMode(INPUT_PINS[i], INPUT);
  }

  // Initialize LEDs
  for (int i = 0; i < NUM_LEDS; i++) {
    pinMode(LED_PINS[i], OUTPUT);
    digitalWrite(LED_PINS[i], LOW);
  }

  // Initialize MOSFETs
  for (int i = 0; i < NUM_MOSFETS; i++) {
    pinMode(MOSFET_PINS[i], OUTPUT);
    digitalWrite(MOSFET_PINS[i], LOW);
  }

  // Initialize BNC
  for (int i = 0; i < NUM_BNC; i++) {
    pinMode(BNC_PINS[i], OUTPUT);
    digitalWrite(BNC_PINS[i], LOW);
  }

  Serial.println("System Initialized. Ready.");
}

void loop() {
  unsigned long currentMillis = millis();

  // 1. Handle Serial Commands
  if (Serial.available() > 0) {
    String command = Serial.readStringUntil('\n');
    command.trim();
    processCommand(command);
  }

  // 2. Handle MOSFET Timers (Non-blocking)
  for (int i = 0; i < NUM_MOSFETS; i++) {
    if (mosfetActive[i]) {
      if (currentMillis >= mosfetEndTime[i]) {
        // Timer finished - turn off relay
        digitalWrite(MOSFET_PINS[i], LOW);
        mosfetActive[i] = false;
      }
    }
  }

  // 3. Handle BNC Timers (Non-blocking)
  for (int i = 0; i < NUM_BNC; i++) {
    if (bncActive[i]) {
      if (currentMillis >= bncEndTime[i]) {
        digitalWrite(BNC_PINS[i], LOW);
        bncActive[i] = false;
      }
    }
  }

  // 4. Read Inputs and Send Status
  if (currentMillis - lastStatusTime >= STATUS_INTERVAL) {
    lastStatusTime = currentMillis;
    sendStatus(currentMillis);
  }
}

// --- Helper Functions ---

void sendStatus(unsigned long timestamp) {
  // Collect all active input pin numbers (1-indexed for user-friendliness)
  String activePins = "";
  int activeCount = 0;
  
  for (int i = 0; i < NUM_INPUTS; i++) {
    if (digitalRead(INPUT_PINS[i]) == HIGH) {
      if (activeCount > 0) {
        activePins += ",";  // Separate multiple pins with comma
      }
      activePins += String(i + 1);  // Pin ID is 1-8 (input index + 1)
      activeCount++;
    }
  }
  
  // If no pins are active, report 0
  if (activeCount == 0) {
    activePins = "0";
  }

  // Format: STATUS:<timestamp>:<active_pin_numbers>
  // Examples: STATUS:1234567890:0 (no inputs), STATUS:1234567890:2 (pin 2), STATUS:1234567890:2,4,7 (multiple)
  Serial.print("STATUS:");
  Serial.print(timestamp);
  Serial.print(":");
  Serial.println(activePins);
}

void processCommand(String cmd) {
  // Parse command format: TYPE:ARG1:ARG2...
  int firstColon = cmd.indexOf(':');
  if (firstColon == -1) return;

  String type = cmd.substring(0, firstColon);
  String args = cmd.substring(firstColon + 1);

  if (type == "LED") {
    handleLED(args);
  } else if (type == "MOS") {
    handleMOSFET(args);
  } else if (type == "BNC") {
    handleBNC(args);
  } else {
    Serial.println("Error: Unknown command type. Use LED, MOS, or BNC.");
  }
}

void handleLED(String args) {
  // Format: ID:STATE (e.g., 1:ON or 3:OFF)
  int firstSep = args.indexOf(':');
  if (firstSep == -1) return;

  int id = args.substring(0, firstSep).toInt();
  String state = args.substring(firstSep + 1);

  if (id < 1 || id > NUM_LEDS) {
    Serial.println("Error: LED ID out of range (1-8).");
    return;
  }

  int pinIndex = id - 1;
  int pin = LED_PINS[pinIndex];

  if (state == "ON" || state == "1") {
    digitalWrite(pin, HIGH);
  } else if (state == "OFF" || state == "0") {
    digitalWrite(pin, LOW);
  } else {
    // Try to parse as PWM value (0-255) if the user sends a number
    int val = state.toInt();
    if (val >= 0 && val <= 255) {
      analogWrite(pin, val);
    } else {
      Serial.println("Error: Invalid LED state. Use ON, OFF, or 0-255.");
    }
  }
}

void handleMOSFET(String args) {
  // Format: ID:MODE:DURATION
  // Example: 1:ON:5000 (Pin 1, ON for 5 seconds)
  // Example: 2:ON:0 (Pin 2, ON continuously until turned OFF)
  // Example: 3:OFF:0 (Pin 3, OFF immediately)
  
  int sep1 = args.indexOf(':');
  if (sep1 == -1) return;
  int id = args.substring(0, sep1).toInt();
  String rest = args.substring(sep1 + 1);

  int sep2 = rest.indexOf(':');
  if (sep2 == -1) return;
  String mode = rest.substring(0, sep2);
  int duration = rest.substring(sep2 + 1).toInt();

  if (id < 1 || id > NUM_MOSFETS) {
    Serial.println("Error: MOSFET ID out of range (1-16).");
    return;
  }

  int pinIndex = id - 1;
  int pin = MOSFET_PINS[pinIndex];

  if (mode == "ON") {
    digitalWrite(pin, HIGH);
    // Set timer if duration > 0 (timed pulse)
    if (duration > 0) {
      mosfetActive[pinIndex] = true;
      mosfetEndTime[pinIndex] = millis() + duration;
    } else {
      // Continuous ON - no auto-turnoff
      mosfetActive[pinIndex] = false;
    }
  } else if (mode == "OFF") {
    digitalWrite(pin, LOW);
    mosfetActive[pinIndex] = false;
  } else {
    Serial.println("Error: Invalid MOS mode. Use ON or OFF.");
  }
}

void handleBNC(String args) {
  // Format: ID:PULSE:DURATION
  // Example: 1:PULSE:100 (Pin 23, 100ms pulse)
  
  int sep1 = args.indexOf(':');
  if (sep1 == -1) return;
  int id = args.substring(0, sep1).toInt();
  String rest = args.substring(sep1 + 1);

  int sep2 = rest.indexOf(':');
  if (sep2 == -1) return;
  String action = rest.substring(0, sep2);
  int duration = rest.substring(sep2 + 1).toInt();

  if (id < 1 || id > NUM_BNC) {
    Serial.println("Error: BNC ID out of range (1-2).");
    return;
  }

  if (action != "PULSE") {
    Serial.println("Error: BNC only supports PULSE command.");
    return;
  }

  int pin = BNC_PINS[id - 1];
  
  // Trigger Pulse (non-blocking)
  digitalWrite(pin, HIGH);
  bncActive[id-1] = true;
  bncEndTime[id-1] = millis() + duration;
}

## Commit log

2026-03-26 Restructuring Portmaster Folder
    [MasterModulePCB.brd, SchematicMasterModulePCB.sch, copper_bottom_l4.gbr, copper_inner_l2.gbr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]
2026-03-31 started working on camera controls
2026-04-01 started implementing camera functionality
2026-04-01 Fixed camera_on
2026-04-07 Camera live replay is working now
